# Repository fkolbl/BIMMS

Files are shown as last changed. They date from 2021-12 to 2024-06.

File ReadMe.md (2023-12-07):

# BIMMS
*Python library for controling [BIMMS](https://www.hardware-x.com/article/S2468-0672(22)00132-8/fulltext)*.

# Installation

use pip for installation : 
```
pip install bimms
```

# Requirements

Third party software (Waveform) has to be installed before BIMMS python API. 
BIMMS has been developped for python 3.
Required packages:
- numpy
- scipy
- matplotlib
- andi-py

for the third party softwares, please visit:
[Waveform](https://digilent.com/shop/software/digilent-waveforms/)

# TODO
    - Add selftests capabilities 
    - Add calibration routines --> skeleton OK 
    - Comments
    - add verbosity mode
    - do "standard configuration" 
    - add check_saturation 
    - add auto HIGH/LOW GAIN 
    - offset compensation in scope input

# HARDWARE TEST TODO:
    - Double check excitation/readout signaling 
    - test connect_TIA_to_CH2, disconnect_TIA_from_CH2, disable_current_source, enable_potentiostat
    - test dc feedback
    - Offset values are odds (measure seems ok tho)
    - Test Readout AC coupling (IA, TIA, etc) --> TIA AC COupling???

# Calibration todo
    - Offset calibration
    - DC calibration
    - OSL calibration

#TODO CONF AD2:
#SET in_channel_range_set --> 2.0,5.0 or 5.0 --> 2.0 by default; check if saturation?
#BS.ad2.in_average_filter_mode(-1)
#AD2 attenation = 1.0
#AD2 offsets = 0.0 
#Triggers --> AWG by default --> external TODO
#Conf modes (bode,)

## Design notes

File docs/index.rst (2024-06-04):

.. NeuRon Virtualizer (NRV) documentation master file, created by
   sphinx-quickstart on Sun Jul 23 14:36:32 2023.
   You can adapt this file completely to your liking, but it should at least
   contain the root `toctree` directive.

Welcome to BIMMS controling library's documentation!
====================================================

NRV (or NeuRon Virtualizer) is a pythonic framework to enable fast and user-friendly simulations of the Peripheral Nervous System. Axons models are simulated with the NEURON software, and extracellular fields are computed either from analytic equations such as point source approximation or with a more detailed description of the nerve and electrode geometry and Finite Elements Method, either using COMSOL (additional commercial license required) or the FENICS project. All computations are performed with the quasi-static approximation of the Maxwell equations, no ephaptic coupling. Stimulation waveform can be of random shapes, and any kinds of electrode can be combined to model complex stimulation strategies.

NRV is optimized for large population of axons, from generating correct population following a specific diameter distribution, through automatic placement to computation and post-processing of the axons' activity when a stimulus is applied. Parallel computation, interface with NEURON and COMSOL and FENICS is automatically handled by NRV.

NRV was developed by contributors from the CELL research group at the Laboratory ETIS (UMR CNRS 8051), ENSEA - CY Cergy Paris University, until june 2023 and is now developed and maintained by the Bioelectronics group of laboratory IMS (UMR CNRS 5218), INP Bordeaux, U. Bordeaux.

.. toctree::
   :maxdepth: 2
   :caption: Contents:

   introduction
..    installation
..    modules
..    changelog
..    devcorner

Indices and tables
==================

* :ref:`genindex`
* :ref:`modindex`
* :ref:`search`

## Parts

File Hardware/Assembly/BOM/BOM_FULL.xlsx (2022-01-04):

Designator | Qty | Manufacturer | Mfg Part | Description / Value | Package/Footprint
Q27,Q26 | 2 | Nexperia | PMT200EPEX | MOSFET 70V N- CHANNEL | SOT-223-3
Y1 | 1 | ABRACON | ABM8W-16.0000MHZ-7-D1X-T3 | Quartz CRYSTAL 16.0000MHZ 7PF SMD | 3.2x2.5mm
RV2 | 1 | Bourns | 3214W-1-503E | Trimmer Resistors SMD 4mm SQ 50K OHM | 3214J
RV1 | 1 | Bourns | 3214W-1-103E | Trimmer Resistors SMD 4mm SQ 10K OHM | 3214J
U8,U11,U12,U9 | 4 | Analog Devices | AD8250ARMZ | Amplificateurs d’instrumentation Hi Speed Programmable Gain In-Amp | MSOP-10
Q2,Q5,Q25,Q24,Q23,Q22,Q21,Q20,Q19,Q18,Q15,Q14,Q13,Q12,Q11,Q10,Q9,Q8,Q7,Q6,Q4,Q3,Q1 | 23 | Nexperia | NXV55UNR | MOSFET NCH 1A 100V 500MOHMS CPH3 | SOT-23-3
R38,R39,R75,R58,R12 | 5 | any/open | any/open | RES 1K OHM 1/8W 1% 0603 SMD | R_0603
R28,R27,R32,R31,R61,R60 | 6 | any/open | any/open | RES 39K OHM 1/8W 1% 0603 SMD | R_0603
K2,K5,K3,K23,K22,K21,K20,K19,K18,K17,K16,K15,K14,K13,K12,K11,K10,K9,K8,K7,K6,K4,K1 | 24 | KEMET | EE2-5NUH-L | Low Signal Relays - PCB 5V 10uA Relay Signal 2formC | EE2
R22,R50,R51,R23,R79,R106,R104,R102,R99,R98,R95,R92,R90,R88,R83,R78,R77,R73,R72,R71,R66,R64,R37,R10 | 23 | any/open | any/open | RES 100 OHM 1/8W 1% 0603 SMD | R_0603
R13,R15,R17,R14 | 4 | any/open | any/open | RES 10M OHM 1/8W 1% 0603 SMD | R_0603
R16,R20,R52,R48,R24,R44,R53,R49,R45,R25,R21,R18,R84,R105,R103,R101,R100,R97,R96,R94,R91,R89,R87,R82,R80,R76,R74,R70,R69,R65,R63,R35,R9,R5,R4,R1 | 36 | any/open | any/open | RES 10K OHM 1/8W 1% 0603 SMD | R_0603
R26,R29,R40,R46,R47,R41,R33,R30,R62,R59,R7,R6 | 12 | any/open | any/open | RES 4.7K OHM 1/8W 1% 0603 SMD | R_0603
D7,D14,D15,D8,D35,D34,D33,D32,D31,D30,D29,D27,D26,D25,D24,D23,D22,D21,D20,D17,D16,D11,D6 | 23 | ON Semiconductor | MBR0530T1G | Schottky Diodes & Rectifiers 0.5A 30V | SOD-123-2
D12,D9,D13,D10,D5,D4,D3,D1,D36,D28,D19,D18 | 12 | Wurth Elektronik | 150060VS75000 | Standard LEDs - SMD WL-SMCW SMDMono TpVw Waterclr 0603 BrtGrn | LED_0603
C65,C63,C27,C23,C20,C18,C49,C47,C66,C64,C28,C25,C50,C48,C21,C19,C79,C101,C90,C85,C84,C75,C73,C72,C61,C51,C45,C39,C17,C9,C8,C7,C6 | 33 | AVX | TAJB106K020SNJ | Tantalum Capacitors - Solid SMD 20V 10uF 10% 1210 ESR = 2.1 Ohm | CP_1210
C26 | 1 | any/open | any/open | MLCC - SMD/SMT 50V 4.7pF C0G 0603 | C_0603
C68,C67,C33,C31,C42,C41,C29,C22,C54,C52,C70,C69,C34,C32,C55,C53,C44,C43,C30,C24,C102,C100,C98,C97,C95,C94,C93,C92,C91,C89,C87,C86,C83,C82,C81,C78,C77,C76,C62,C56,C46,C40,C16,C15,C14,C13,C12,C11,C10,C4,C1 | 51 | any/open | any/open | CAP CER 100 nF 25V X7R 0603 | C_0603_1608Metric
C36,C35,C38,C37,C99,C96,C74,C71 | 8 | any/open | any/open | CAP CER 1 uF 25V X7R 0603 | C_0603_1608Metric
U5,U14,U6 | 3 | Analog Devices | LT1964ES5-BYP#TRPBF | LDO Voltage Regulators 200mA L/N Negative LDO in Thin SOT | TSOT-23-5
U3,U13,U4 | 3 | Analog Devices | LT1962EMS8#TRPBF | LDO Voltage Regulators 300mA Low Noise LDO | MSOP-8
U21 | 1 | Texas Instruments | TLV70233PDBVR | LDO Voltage Regulators 300mA Low-IQ LDO Reg | SOT-23-5
U20 | 1 | STMicroelectronics | STM32F103C6T6A | ARM Microcontrollers - MCU 32BIT Cortex M3 M/D 32 to 128 USB/CAN | LQFP-64
U16 | 1 | Analog Devices | LTC4416EMS#PBF | Power Management Specialised PMIC Dual PowerPath Controller | MSOP-10
U2 | 1 | Texas Instruments | OPA192IDR | Precision Amplifiers High VTG RRIO Prec Op Amps E-Trim | SOIC-8
SW3,SW2,SW1 | 3 | E-Switch | TL3305AF160QG | Tactile Switches 50mA 12VDC SPST, NO 3.8mm Act 160gf | 4.5x4.5 mm
R108,R107,R8,R3,R2 | 5 | any/open | any/open | RES 2K OHM 1/8W 1% 0603 SMD | R_0603_1608Metric
R93 | 1 | any/open | any/open | RES 3K3 OHM 1/8W 1% 0603 SMD | R_0603_1608Metric
R81 | 1 | any/open | any/open | RES 27 OHM 1/8W 1% 0603 SMD | R_0603_1608Metric
R56 | 1 | any/open | any/open | RES 1K OHM 1/8W 1% 0603 SMD | R_0603_1608Metric
R43,R42,R36,R34 | 4 | any/open | any/open | RES 390 OHM 1/8W 1% 0603 SMD | R_0603_1608Metric
R19 | 1 | any/open | any/open | RES 1K2 OHM 1/8W 1% 0603 SMD | R_0603_1608Metric
R11 | 1 | any/open | any/open | RES 1K8 OHM 1/8W 1% 0603 SMD | R_0603_1608Metric
L1,L3,L2 | 3 | Taiyo Yuden | CBC3225T100KR | Fixed Inductors 1210 10uH 172.9mOhms +/-10% 900mA HiCur | L_1210
C88 | 1 | any/open | any/open | CAP CER 4.7 nF 25V X7R 0603 | C_0603_1608Metric
C60,C59 | 2 | any/open | any/open | MLCC - SMD/SMT 50V 1pF C0G 0603 | C_0603_1608Metric
C5,C3 | 2 | any/open | any/open | MLCC - SMD/SMT 50V 30pF C0G 0603 | C_0603_1608Metric
U18,U17 | 2 | Analog Devices | AD830ARZ | Differential Amplifiers SOIC HI SPD, VIDEO DIFF OP AMP | SOIC-8
U15,U7 | 2 | Texas Instruments | THS4631 | High Speed Operational Amplifiers High Speed FET-Input Op Amp | SOIC-8
U10 | 1 | Texas Instruments | THS4151IDGK | Differential Amplifiers Fully Differential I/O High Slew Rate | VSSOP-8
R55,R54 | 2 | any/open | any/open | RES 10R OHM 1/8W 1% 0603 SMD | R_0603_1608Metric
D2,D37 | 2 | Wurth Elektronik | 150060SS55040 | Standard LEDs - SMD WL-SMCD SMD MonoChip 0603 Super Red 645nm | LED_0603
C57,C58 | 2 | any/open | any/open | MLCC - SMD/SMT 50V 10pF C0G 0603 | C_0603_1608Metric
R109 | 1 | any/open | any/open | RES 47k OHM 1/8W 1% 0603 SMD | R_0603_1608Metric
R68,R67 | 2 | any/open | any/open | RES 5k1 OHM 1/8W 1% 0603 SMD | R_0603_1608Metric
R57 | 1 | any/open | any/open | RES 1M OHM 1/8W 1% 0603 SMD | R_0603_1608Metric
U1 | 1 | tracopower | TDN 5-0922WI | TDN 5-0922WI | TDN 5-0922WI
U19 | 1 | tracopower | TEC 3-0911 | TEC_3-0911 | TEC 3-0910
C2 | 1 | any/open | any/open | 220 uF 25V | CP_Radial_D8.0mm_P5.00mm
J19,J9,J30,J31,J26,J28,J25,J27,J22,J21,J20,J10,J8,J7,J6,J29 | 16 | any/open | any/open | PCB Vertical SMA | PCB Vertical SMA
J4,J15,J5 | 3 | any/open | any/open | PinHeader_2x02_P2.54mm_Vertical | PinHeader_2x02_P2.54mm_Vertical
J33 | 1 | any/open | any/open | PinHeader_1x06_P2.54mm_Horizontal | PinHeader_1x06_P2.54mm_Horizontal
J18 | 1 | any/open | any/open | PinHeader_2x07_P2.54mm_Horizontal | PinHeader_2x07_P2.54mm_Horizontal
J16,JP4,JP3 | 3 | any/open | any/open | PinHeader_1x02_P2.54mm_Vertical | PinHeader_1x02_P2.54mm_Vertical
J32 | 1 | any/open | any/open | PinSocket_2x15_P2.54mm_Horizontal | PinSocket_2x15_P2.54mm_Horizontal
J29 | 1 | any/open | any/open | PinHeader_2x15_P2.54mm_Vertical | PinHeader_2x15_P2.54mm_Vertical
J23 | 1 | any/open | any/open | TerminalScrew_1x04_P2.54mm_Vertical | TerminalScrew_1x04_P2.54mm_Vertical
J13,J14,J24 | 3 | any/open | any/open | PinSocket_1x04_P2.54mm_Horizontal | PinSocket_1x04_P2.54mm_Horizontal
J11,J12 | 2 | any/open | any/open | PinSocket_2x03_P2.54mm_Horizontal | PinSocket_2x03_P2.54mm_Horizontal
J3 | 1 | any/open | any/open | PinSocket_1x03_P2.54mm_Horizontal | PinSocket_1x03_P2.54mm_Horizontal
J2 | 1 | any/open | any/open | PinHeader_2x05_P1.27mm_Vertical_SMD | PinHeader_2x05_P1.27mm_Vertical_SMD
J1 | 1 | CUI Devices | PJ-063BH | BarrelJack_CUI_PJ-063AH_Horizontal | BarrelJack_CUI_PJ-063AH_Horizontal
J17 | 1 | XKB Connectivity | U262-161N-4BVC11 | USB_C_Receptacle_XKB_U262-16XN-4BVC11 | USB_C_Receptacle_XKB_U262-16XN-4BVC11
F1 | 1 | any/open | any/open | Fuse_1206_3216Metric_Pad1.42x1.75mm_HandSolder | Fuse_1206_3216Metric_Pad1.42x1.75mm_HandSolder
Spacers Analog Discovery 2 | 4 | any/open | any/open | M3 x 10mm Fem/Fem | M3 x 10mm Fem/Fem
Spacers Board | 6 | any/open | any/open | M3 x 20mm Fem/Fem | M3 x 20mm Fem/Fem
Con Analog Discovery 2 | 2 | any/open | any/open | Headers & Wire Housings .1CL IDC REC 2X15P MIL 30AU | Headers & Wire Housings .1CL IDC REC 2X15P MIL 30AU
PCB screws | 20 | any/open | any/open | M3 x 4mm | M3 x 4mm

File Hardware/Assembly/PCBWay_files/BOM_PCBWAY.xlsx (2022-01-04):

 |  |  | xxxx xxxx xxxxx xxPCS BOM (Sample Bill of Materials)
Item # | *Designator | *Qty | Manufacturer | *Mfg Part # | Description / Value | *Package/Footprint | Type | Your Instructions / Notes
1 | Q26,Q27 | 2 | Nexperia | PMT200EPEX | MOSFET 70V N- CHANNEL | SOT-223-3 | SMD
2 | Y1 | 1 | ABRACON | ABM8W-16.0000MHZ-7-D1X-T3 | Quartz CRYSTAL 16.0000MHZ 7PF SMD | 3.2x2.5mm | SMD
3 | RV2 | 1 | Bourns | 3214W-1-503E | Trimmer Resistors SMD 4mm SQ 50K OHM | 3214J | SMD
4 | RV1 | 1 | Bourns | 3214W-1-103E | Trimmer Resistors SMD 4mm SQ 10K OHM | 3214J | SMD
5 | U8,U11,U12,U9 | 4 | Analog Devices | AD8250ARMZ | Amplificateurs d’instrumentation Hi Speed Programmable Gain In-Amp | MSOP-10 | SMD
6 | Q2,Q5,Q25,Q24,Q23,Q22,Q21,Q20,Q19,Q18,Q15,Q14,Q13,Q12,Q11,Q10,Q9,Q8,Q7,Q6,Q4,Q3,Q1 | 23 | Nexperia | NXV55UNR | MOSFET NCH 1A 100V 500MOHMS CPH3 | SOT-23-3 | SMD
7 | R38,R39,R75,R58,R12 | 5 | any/open | any/open | RES 1K OHM 1/8W 1% 0603 SMD | R_0603 | SMD
8 | R28,R27,R32,R31,R61,R60 | 6 | any/open | any/open | RES 39K OHM 1/8W 1% 0603 SMD | R_0603 | SMD
9 | K2,K5,K3,K23,K22,K21,K20,K19,K18,K17,K16,K15,K14,K13,K12,K11,K10,K9,K8,K7,K6,K4,K1 | 23 | KEMET | EE2-5NUH-L | Low Signal Relays - PCB 5V 10uA Relay Signal 2formC | EE2 | SMD
10 | R22,R50,R51,R23,R79,R106,R104,R102,R99,R98,R95,R92,R90,R88,R83,R78,R77,R73,R72,R71,R66,R64,R37,R10 | 24 | any/open | any/open | RES 100 OHM 1/8W 1% 0603 SMD | R_0603 | SMD
11 | R13,R15,R17,R14 | 4 | any/open | any/open | RES 10M OHM 1/8W 1% 0603 SMD | R_0603 | SMD
12 | R16,R20,R52,R48,R24,R44,R53,R49,R45,R25,R21,R18,R84,R105,R103,R101,R100,R97,R96,R94,R91,R89,R87,R82,R80,R76,R74,R70,R69,R65,R63,R35,R9,R5,R4,R1 | 36 | any/open | any/open | RES 10K OHM 1/8W 1% 0603 SMD | R_0603 | SMD
13 | R26,R29,R40,R46,R47,R41,R33,R30,R62,R59,R7,R6 | 12 | any/open | any/open | RES 4.7K OHM 1/8W 1% 0603 SMD | R_0603 | SMD
14 | D7,D14,D15,D8,D35,D34,D33,D32,D31,D30,D29,D27,D26,D25,D24,D23,D22,D21,D20,D17,D16,D11,D6 | 23 | ON Semiconductor | MBR0530T1G | Schottky Diodes & Rectifiers 0.5A 30V | SOD-123-2 | SMD
15 | D12,D9,D13,D10,D5,D4,D3,D1,D36,D28,D19,D18 | 12 | Wurth Elektronik | 150060VS75000 | Standard LEDs - SMD WL-SMCW SMDMono TpVw Waterclr 0603 BrtGrn | LED_0603 | SMD
16 | C65,C63,C27,C23,C20,C18,C49,C47,C66,C64,C28,C25,C50,C48,C21,C19,C79,C101,C90,C85,C84,C75,C73,C72,C61,C51,C45,C39,C17,C9,C8,C7,C6 | 33 | AVX | TAJB106K020SNJ | Tantalum Capacitors - Solid SMD 20V 10uF 10% 1210 ESR = 2.1 Ohm | CP_1210 | SMD
17 | C26 | 1 | any/open | any/open | MLCC - SMD/SMT 50V 4.7pF C0G 0603 | C_0603 | SMD
18 | C68,C67,C33,C31,C42,C41,C29,C22,C54,C52,C70,C69,C34,C32,C55,C53,C44,C43,C30,C24,C102,C100,C98,C97,C95,C94,C93,C92,C91,C89,C87,C86,C83,C82,C81,C78,C77,C76,C62,C56,C46,C40,C16,C15,C14,C13,C12,C11,C10,C4,C1 | 51 | any/open | any/open | CAP CER 100 nF 25V X7R 0603 | C_0603_1608Metric | SMD
19 | C36,C35,C38,C37,C99,C96,C74,C71 | 8 | any/open | any/open | CAP CER 1 uF 25V X7R 0603 | C_0603_1608Metric | SMD
20 | U5,U14,U6 | 3 | Analog Devices | LT1964ES5-BYP#TRPBF | LDO Voltage Regulators 200mA L/N Negative LDO in Thin SOT | TSOT-23-5 | SMD
21 | U3,U13,U4 | 3 | Analog Devices | LT1962EMS8#TRPBF | LDO Voltage Regulators 300mA Low Noise LDO | MSOP-8 | SMD
22 | U21 | 1 | Texas Instruments | TLV70233PDBVR | LDO Voltage Regulators 300mA Low-IQ LDO Reg | SOT-23-5 | SMD
23 | U20 | 1 | STMicroelectronics | STM32F103R6T6A | ARM Microcontrollers - MCU 32BIT Cortex M3 M/D 32 to 128 USB/CAN | LQFP-64 | SMD
24 | U16 | 1 | Analog Devices | LTC4416EMS#PBF | Power Management Specialised PMIC Dual PowerPath Controller | MSOP-10 | SMD
25 | U2 | 1 | Texas Instruments | OPA192IDR | Precision Amplifiers High VTG RRIO Prec Op Amps E-Trim | SOIC-8 | SMD
26 | SW3,SW2,SW1 | 3 | E-Switch | TL3305AF160QG | Tactile Switches 50mA 12VDC SPST, NO 3.8mm Act 160gf | 4.5x4.5 mm | SMD
27 | R108,R107,R8,R3,R2 | 5 | any/open | any/open | RES 2K OHM 1/8W 1% 0603 SMD | R_0603_1608Metric | SMD
28 | R93 | 1 | any/open | any/open | RES 3K3 OHM 1/8W 1% 0603 SMD | R_0603_1608Metric | SMD
29 | R81 | 1 | any/open | any/open | RES 27 OHM 1/8W 1% 0603 SMD | R_0603_1608Metric | SMD
30 | R56 | 1 | any/open | any/open | RES 1K OHM 1/8W 1% 0603 SMD | R_0603_1608Metric | SMD
31 | R43,R42,R36,R34 | 4 | any/open | any/open | RES 390 OHM 1/8W 1% 0603 SMD | R_0603_1608Metric | SMD
32 | R19 | 1 | any/open | any/open | RES 1K2 OHM 1/8W 1% 0603 SMD | R_0603_1608Metric | SMD
33 | R11 | 1 | any/open | any/open | RES 1K8 OHM 1/8W 1% 0603 SMD | R_0603_1608Metric | SMD
34 | L1,L3,L2 | 3 | Taiyo Yuden | CBC3225T100KR | Fixed Inductors 1210 10uH 172.9mOhms +/-10% 900mA HiCur | L_1210 | SMD
35 | C88 | 1 | any/open | any/open | CAP CER 4.7 nF 25V X7R 0603 | C_0603_1608Metric | SMD
36 | C60,C59 | 2 | any/open | any/open | MLCC - SMD/SMT 50V 1pF C0G 0603 | C_0603_1608Metric | SMD
37 | C5,C3 | 2 | any/open | any/open | MLCC - SMD/SMT 50V 30pF C0G 0603 | C_0603_1608Metric | SMD
38 | U18,U17 | 2 | Analog Devices | AD830ARZ | Differential Amplifiers SOIC HI SPD, VIDEO DIFF OP AMP | SOIC-8 | SMD
39 | U15,U7 | 2 | Texas Instruments | THS4631D | High Speed Operational Amplifiers High Speed FET-Input Op Amp | SOIC-8 | SMD
40 | U10 | 1 | Texas Instruments | THS4151IDGNR | Differential Amplifiers Fully Differential I/O High Slew Rate | VSSOP-8 | SMD
41 | R55,R54 | 2 | any/open | any/open | RES 10R OHM 1/8W 1% 0603 SMD | R_0603_1608Metric | SMD
42 | D2,D37 | 2 | Wurth Elektronik | 150060SS55040 | Standard LEDs - SMD WL-SMCD SMD MonoChip 0603 Super Red 645nm | LED_0603 | SMD
43 | C57,C58 | 2 | any/open | any/open | MLCC - SMD/SMT 50V 10pF C0G 0603 | C_0603_1608Metric | SMD
44 | R109 | 1 | any/open | any/open | RES 47k OHM 1/8W 1% 0603 SMD | R_0603_1608Metric | SMD
45 | R68,R67 | 2 | any/open | any/open | RES 5k1 OHM 1/8W 1% 0603 SMD | R_0603_1608Metric | SMD
46 | R57 | 1 | any/open | any/open | RES 1M OHM 1/8W 1% 0603 SMD | R_0603_1608Metric | SMD

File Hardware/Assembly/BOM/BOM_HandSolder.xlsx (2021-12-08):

Designator | Package | Quantity | Designation | Supplier | Ref | unit Price | Price
U1 | TDN 5-0922WI | 1 | TDN 5-0922WI | Mouser | 495-TDN5-0922WI | 22.02 | 22.02
U19 | TEC 3-0910 | 1 | TEC_3-0911 | Mouser | 495-TEC3-0911 | 10.27 | 10.27
C2 | CP_Radial_D8.0mm_P5.00mm | 1 | 220 uF 25V | Mouser | 661-ELXZ250ETC221MH1 | 0.508 | 0.508
J19,J9,J30,J31,J26,J28,J25,J27,J22,J21,J20,J10,J8,J7,J6,J29 | PCB Vertical SMA | 16 | PCB Vertical SMA | Mouser | 471-SMACONNECTOR | 1.33 | 21.28
J4,J15,J5 | PinHeader_2x02_P2.54mm_Vertical | 3 | PinHeader_2x02_P2.54mm_Vertical | Mouser | 571-5-146250-2 | 0.306 | 0.918
J33 | PinHeader_1x06_P2.54mm_Horizontal | 1 | PinHeader_1x06_P2.54mm_Horizontal | Mouser | 571-826947-6 | 0.5 | 0.5
J18 | PinHeader_2x07_P2.54mm_Horizontal | 1 | PinHeader_2x07_P2.54mm_Horizontal | Mouser | 200-SSQ10702GDRA | 2.24 | 2.24
J16,JP4,JP3 | PinHeader_1x02_P2.54mm_Vertical | 3 | PinHeader_1x02_P2.54mm_Vertical | Mouser | 571-826936-2 | 0.207 | 0.621
J32 | PinSocket_2x15_P2.54mm_Horizontal | 1 | PinSocket_2x15_P2.54mm_Horizontal | Mouser | 200-SSQ11502TDRA | 2.57 | 2.57
J29 | PinHeader_2x15_P2.54mm_Vertical | 1 | PinHeader_2x15_P2.54mm_Vertical | Mouser | 649-77313-801-30LF | 0.99 | 0.99
J23 | Molex_KK-254_AE-6410-04A_1x04_P2.54mm_Vertical | 1 | Molex_KK-254_AE-6410-04A_1x04_P2.54mm_Vertical | Mouser | 571-282834-4 | 2.4 | 2.4
J13,J14,J24 | PinSocket_1x04_P2.54mm_Horizontal | 3 | PinSocket_1x04_P2.54mm_Horizontal | Mouser | 200-SSQ10404SSRA | 1.37 | 4.11
J11,J12 | PinSocket_2x03_P2.54mm_Horizontal | 2 | PinSocket_2x03_P2.54mm_Horizontal | Mouser | 200-SSQ10302GDRA | 1.53 | 3.06
J3 | PinSocket_1x03_P2.54mm_Horizontal | 1 | PinSocket_1x03_P2.54mm_Horizontal | Mouser | 200-SSQ10302SSRA | 0.999 | 0.999
J2 | PinHeader_2x05_P1.27mm_Vertical_SMD | 1 | PinHeader_2x05_P1.27mm_Vertical_SMD | Mouser | 485-752 | 1.27 | 1.27
J1 | BarrelJack_CUI_PJ-063AH_Horizontal | 1 | BarrelJack_CUI_PJ-063AH_Horizontal | Mouser | 490-PJ-063BH | 1.22 | 1.22
J17 | USB_C_Receptacle_XKB_U262-16XN-4BVC11 | 1 | USB_C_Receptacle_XKB_U262-16XN-4BVC11 | LCSC | C319148 | 0.37 | 0.37
F1 | Fuse_1206_3216Metric_Pad1.42x1.75mm_HandSolder | 1 | Fuse_1206_3216Metric_Pad1.42x1.75mm_HandSolder | Mouser | 576-0466.500NR | 0.65 | 0.65
Spacers Analog Discovery 2 | M3 x 10mm Fem/Fem | 4 | M3 x 10mm Fem/Fem | Mouser | 710-970100321 | 0.36 | 1.44
Spacers Board | M3 x 20mm Fem/Fem | 6 | M3 x 20mm Fem/Fem | Mouser | 710-970200354 | 0.567 | 3.402
Con Analog Discovery 2 | Headers & Wire Housings .1CL IDC REC 2X15P MIL 30AU | 2 | Headers & Wire Housings .1CL IDC REC 2X15P MIL 30AU | Mouser | 571-1658623-7 | 2.41 | 4.82
PCB screws | M3 x 4mm | 20 | M3 x 4mm | Mouser | 481-0263 | 0.16 | 3.2

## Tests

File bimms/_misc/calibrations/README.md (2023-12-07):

Here will be store the calibration data in json files

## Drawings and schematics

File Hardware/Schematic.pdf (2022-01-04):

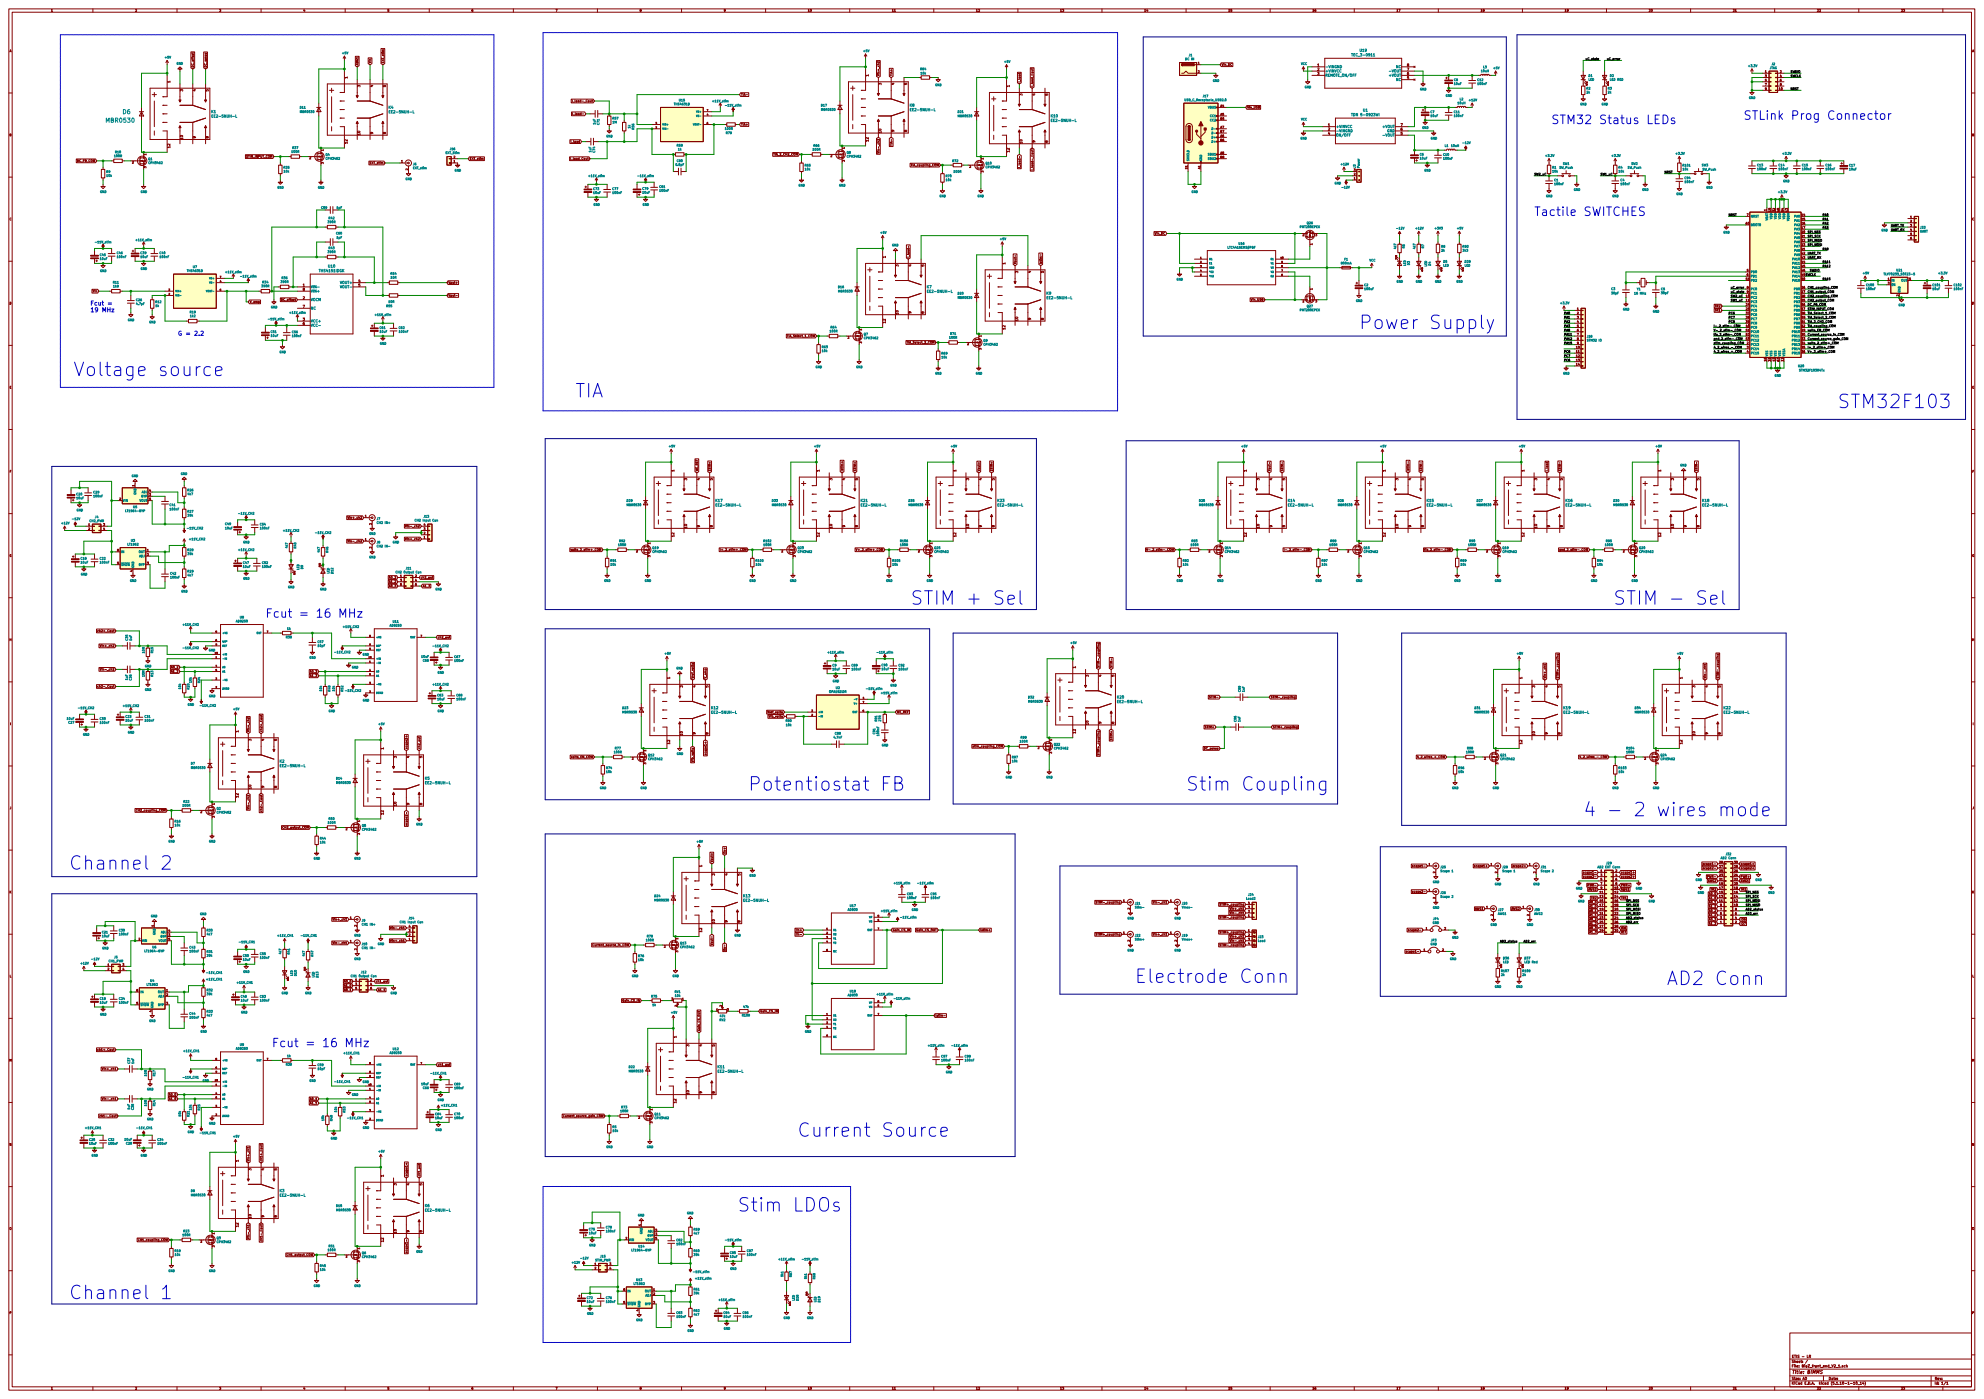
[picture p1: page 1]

STLink Prog Connector STM32 Status LEDs

1 VIN 2 BYP 3 ADJ 4 VOUT 5 U5

scope2- Vin+_ch1 Vin+_ch1 Vin+_ch1 Vin-_ch1

1 VIN 2 BYP 3 ADJ 4 VOUT 5 U6

File: BioZ_front_end_V2_1.sch Sheet: / ETIS - LR

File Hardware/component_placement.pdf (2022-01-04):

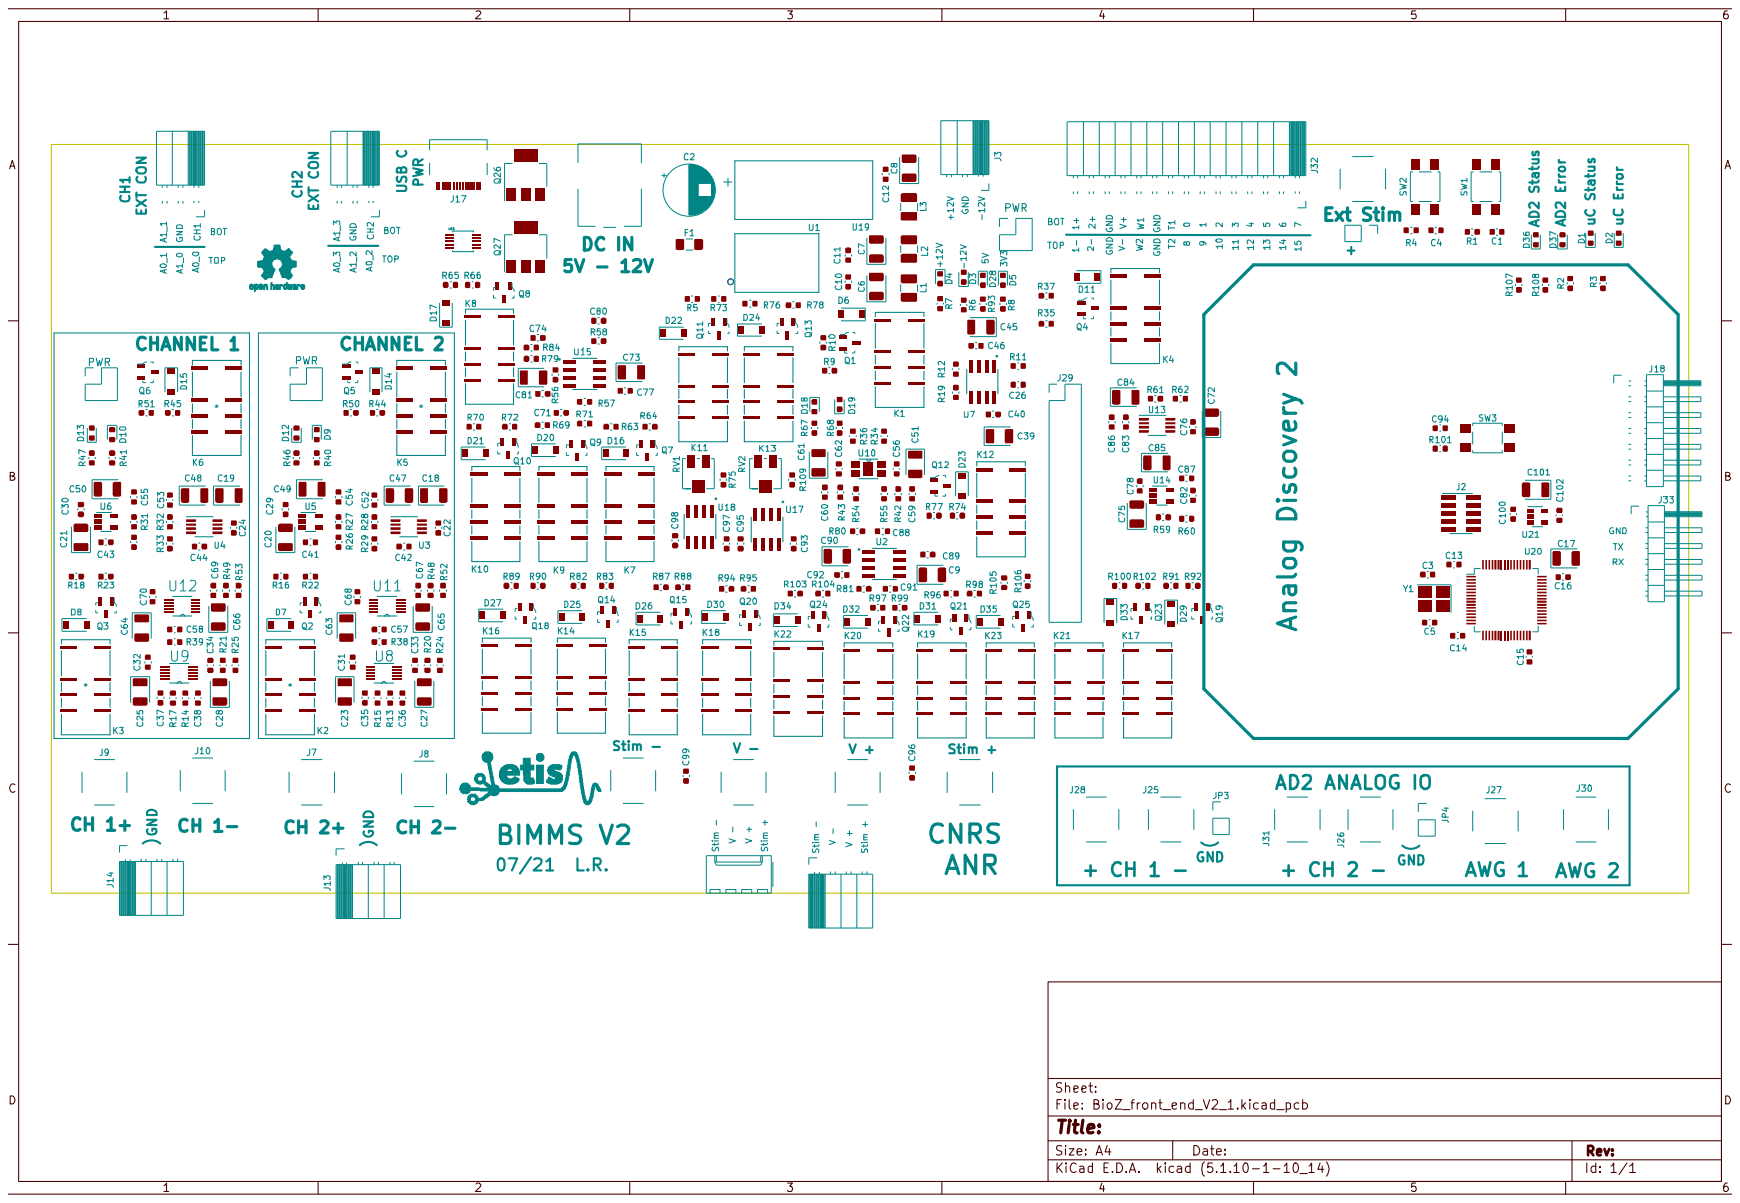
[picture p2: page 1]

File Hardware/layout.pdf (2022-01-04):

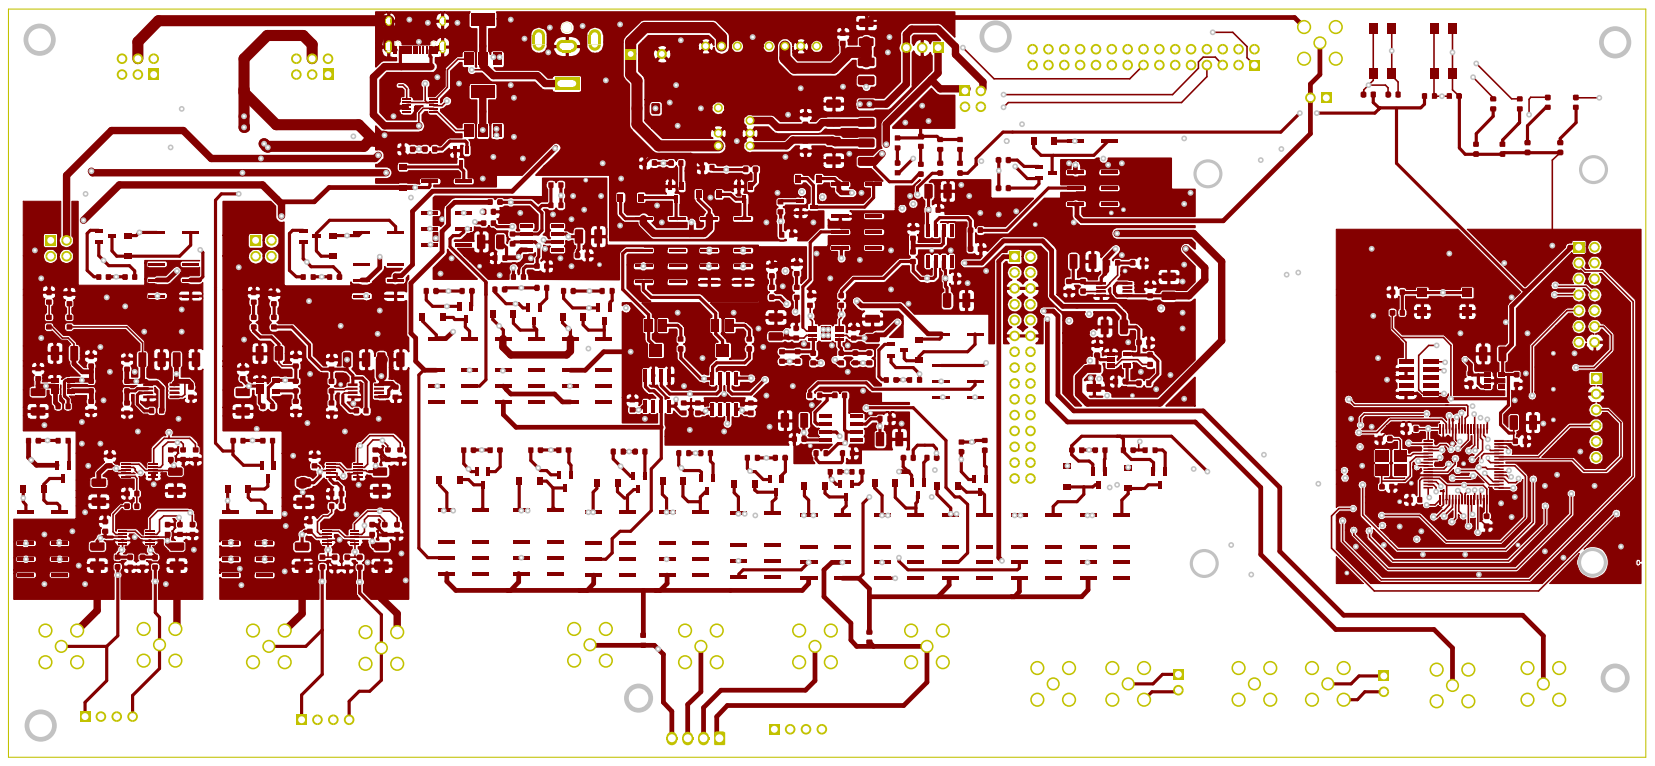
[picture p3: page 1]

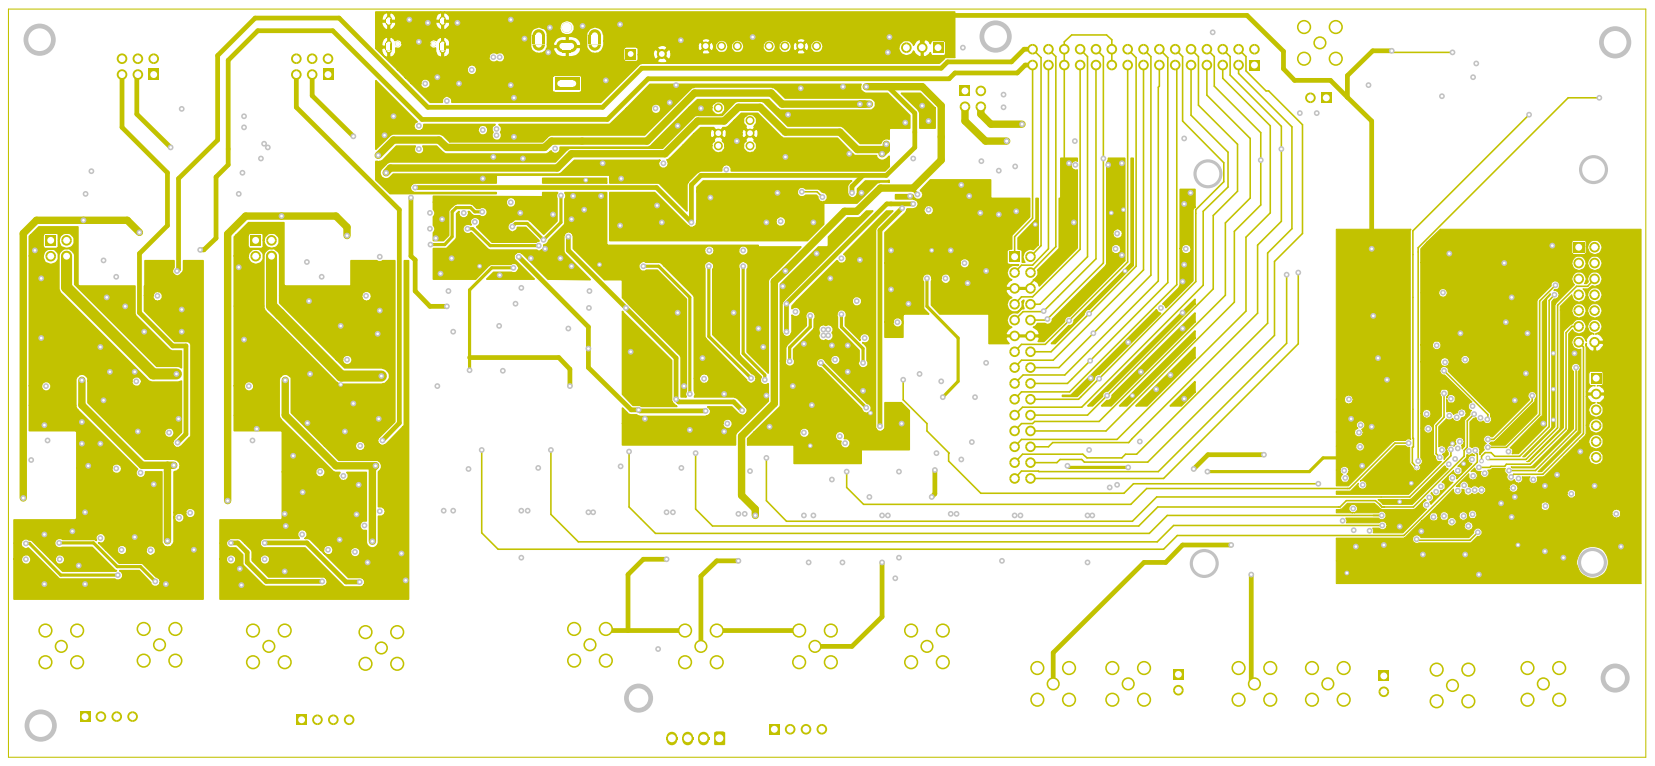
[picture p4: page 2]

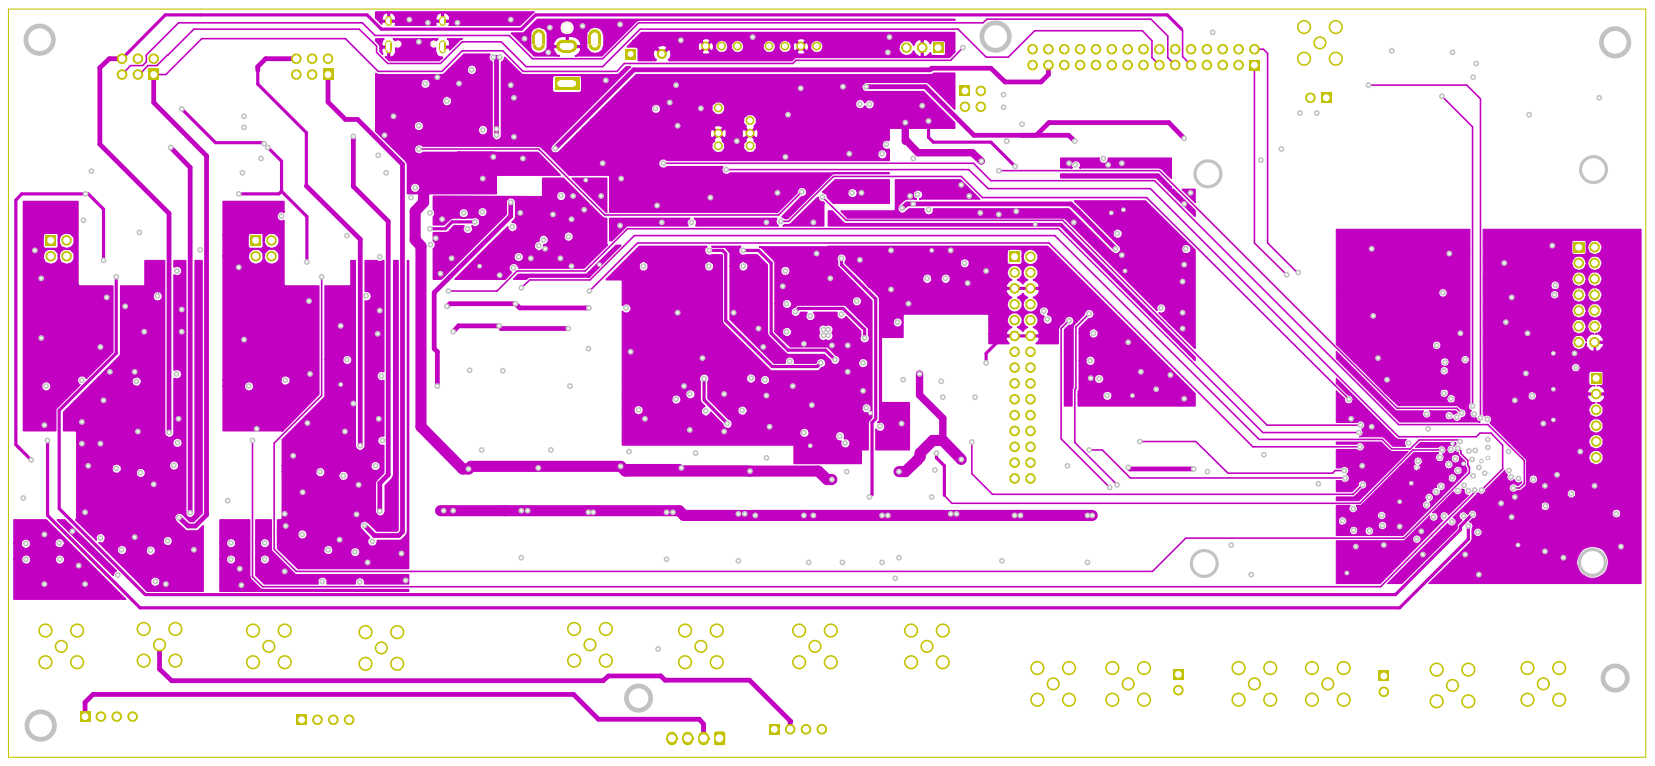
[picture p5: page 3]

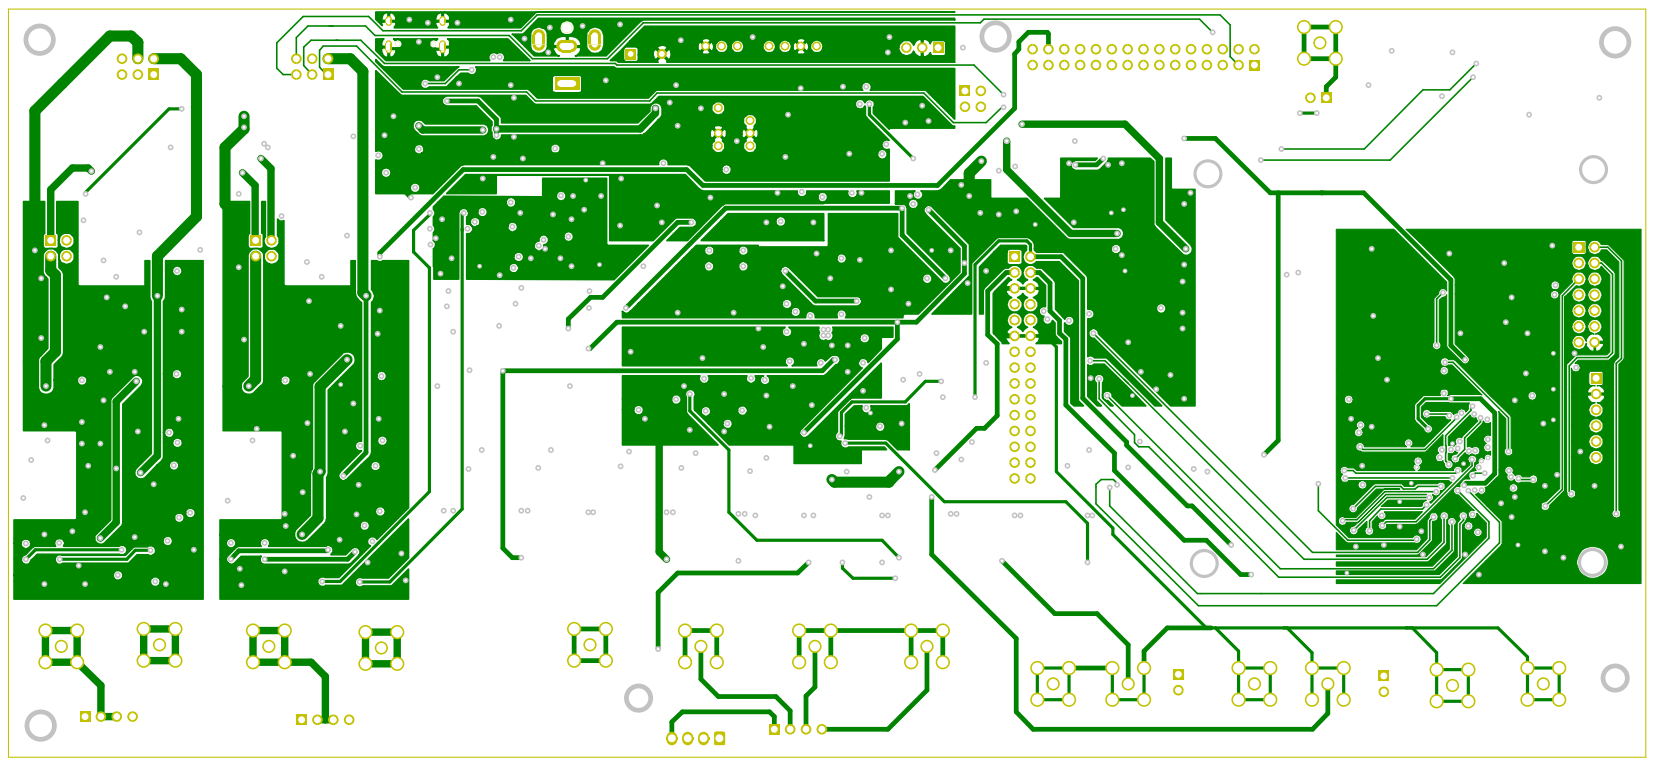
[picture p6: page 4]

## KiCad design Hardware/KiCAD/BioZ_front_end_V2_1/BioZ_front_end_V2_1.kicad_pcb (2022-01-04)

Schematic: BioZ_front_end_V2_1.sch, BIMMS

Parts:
C1, C4, C10, C11, C12, C13, C14, C15, C16, C22, C24, C29, C30, C31, C32, C33, C34, C40, C41, C42, C43, C44, C46, C52, C53, C54, C55, C56, C62, C67, C68, C69, C70, C76, C77, C78, C81, C82, C83, C86, C87, C89, C91, C92, C93, C94, C95, C97, C98, C100, C102: 100nF; C_0603_1608Metric
C2: 100uF; CP_Radial_D8.0mm_P5.00mm
C3, C5: 30pF; C_0603_1608Metric
C6, C7, C8, C9, C17, C18, C19, C20, C21, C23, C25, C27, C28, C39, C45, C47, C48, C49, C50, C51, C61, C63, C64, C65, C66, C72, C73, C75, C79, C84, C85, C90, C101: 10uF; CP_EIA-3528-21_Kemet-B
C26: 4.7pF; C_0603_1608Metric
C35, C36, C37, C38, C71, C74, C96, C99: 1uF; C_0603_1608Metric
C57, C58: 10pF; C_0603_1608Metric
C59, C60: 1pF; C_0603_1608Metric
C80: 0.5pF; C_0603_1608Metric
C88: 4.7nF; C_0603_1608Metric
D1, D3, D4, D5, D9, D10, D12, D13, D18, D19, D28, D36: LED; LED_0603_1608Metric
D2: LED RED; LED_0603_1608Metric
D6, D7, D8, D11, D14, D15, D16, D17, D20, D21, D22, D23, D24, D25, D26, D27, D29, D30, D31, D32, D33, D34, D35: MBR0530; D_SOD-123
D37: LED Red; LED_0603_1608Metric
F1: 800mA; Fuse_1206_3216Metric_Pad1.42x1.75mm_HandSolder
J1: DC IN; BarrelJack_CUI_PJ-063AH_Horizontal
J2: JTAG; PinHeader_2x05_P1.27mm_Vertical_SMD
J3: Power; PinSocket_1x03_P2.54mm_Horizontal; MPN 640456-3; Digi-Key_PN A19470-ND
J4: CH2_PWR; PinHeader_2x02_P2.54mm_Vertical
J5: CH1_PWR; PinHeader_2x02_P2.54mm_Vertical
J6: EXT_stim; SMA_Amphenol_132291_Vertical
J7: CH2 IN+; SMA_Amphenol_132291_Vertical
J8: CH2 IN-; SMA_Amphenol_132291_Vertical
J9: CH1 IN+; SMA_Amphenol_132291_Vertical
J10: CH1 IN-; SMA_Amphenol_132291_Vertical
J11: CH2 Output Con; PinSocket_2x03_P2.54mm_Horizontal
J12: CH1 Output Con; PinSocket_2x03_P2.54mm_Horizontal
J13: CH2 Input Con; PinSocket_1x04_P2.54mm_Horizontal
J14: CH1 Input Con; PinSocket_1x04_P2.54mm_Horizontal
J15: STIM_PWR; PinHeader_2x02_P2.54mm_Vertical
J16: EXT_Stim; PinHeader_1x02_P2.54mm_Vertical
J17: USB_C_Receptacle_USB2.0; USB_C_Receptacle_XKB_U262-16XN-4BVC11
J18: STM32 IO; PinHeader_2x07_P2.54mm_Horizontal
J19: Vmes+; SMA_Amphenol_132291_Vertical
J20: Vmes-; SMA_Amphenol_132291_Vertical
J21: Stim-; SMA_Amphenol_132291_Vertical
J22: Stim+; SMA_Amphenol_132291_Vertical
J23: Load; Molex_KK-254_AE-6410-04A_1x04_P2.54mm_Vertical
J24: Load2; PinSocket_1x04_P2.54mm_Horizontal
J25, J28: Scope 1; SMA_Amphenol_132291_Vertical
J26, J31: Scope 2; SMA_Amphenol_132291_Vertical
J27: AWG1; SMA_Amphenol_132291_Vertical
J29: AD2 EXT Conn; PinHeader_2x15_P2.54mm_Vertical
J30: AWG2; SMA_Amphenol_132291_Vertical
J32: AD2 Conn; PinSocket_2x15_P2.54mm_Horizontal
J33: UART; PinHeader_1x06_P2.54mm_Horizontal
JP3, JP4: GND; PinHeader_1x02_P2.54mm_Vertical
K1, K2, K3, K4, K5, K6, K7, K8, K9, K10, K11, K12, K13, K14, K15, K16, K17, K18, K19, K20, K21, K22, K23: EE2-5NUH-L
L1, L2, L3: 10uH; L_1210_3225Metric_Pad1.42x2.65mm_HandSolder
Q1, Q2, Q3, Q4, Q5, Q6, Q7, Q8, Q9, Q10, Q11, Q12, Q13, Q14, Q15, Q18, Q19, Q20, Q21, Q22, Q23, Q24, Q25: CPH3462
Q26, Q27: PMT200EPEX; SOT-223-3_TabPin2
R1, R4, R5, R9, R16, R18, R20, R21, R24, R25, R35, R44, R45, R48, R49, R52, R53, R63, R65, R69, R70, R74, R76, R80, R82, R84, R87, R89, R91, R94, R96, R97, R100, R101, R103, R105: 10k; R_0603_1608Metric
R2, R3, R8, R107, R108: 2k; R_0603_1608Metric
R6, R7, R26, R29, R30, R33, R40, R41, R46, R47, R59, R62: 4k7; R_0603_1608Metric
R10, R22, R23, R37, R50, R51, R64, R66, R71, R72, R73, R77, R78, R79, R83, R88, R90, R92, R95, R98, R99, R102, R104, R106: 100R; R_0603_1608Metric
R11: 1k8; R_0603_1608Metric
R12, R38, R39, R56, R58, R75: 1k; R_0603_1608Metric
R13, R14, R15, R17: 10M; R_0603_1608Metric
R19: 1k2; R_0603_1608Metric
R27, R28, R31, R32, R60, R61: 39k; R_0603_1608Metric
R34, R36, R42, R43: 390R; R_0603_1608Metric
R54, R55: 10R; R_0603_1608Metric
R57: 1M; R_0603_1608Metric
R67, R68: 5k1; R_0603_1608Metric
R81: 27R; R_0603_1608Metric
R93: 3k3; R_0603_1608Metric
R109: 47k; R_0603_1608Metric
RV1: 10k; Potentiometer_Bourns_3214J_Horizontal
RV2: 47k; Potentiometer_Bourns_3214J_Horizontal
SW1, SW2, SW3: SW_Push; SW_SPST_TL3305A
U1: TDN 5-0923WI; TDN 5-0910WI
U2: OPA192IDR; SOIC127P599X175-8N
U3, U4, U13: LT1962; MSOP-8_3x3mm_P0.65mm
U5, U6, U14: LT1964-BYP; TSOT-23-5
U7, U15: THS4631D; SOIC127P599X175-8N
U8, U9, U11, U12: AD8250; SOP50P490X110-10N
U10: THS4151IDGK
U16: LTC4416EMS#PBF; MSOP-10_MS; MANUFACTURER_PART_NUMBER ltc4416ims1
U17, U18: AD830; SOIC127P600X175-8N
U19: TEC_3-0911; TEC 3-0910
U20: STM32F103R4Tx; LQFP-64_10x10mm_P0.5mm
U21: TLV70233_SOT23-5; SOT-23-5
Y1: 16 MHz; Crystal_SMD_3225-4Pin_3.2x2.5mm_HandSoldering

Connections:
4_2_wires_+_COM: R96.1, R98.2, U20.4 (PC15)
4_2_wires_-_COM: R103.1, R104.2, U20.3 (PC14)
+5VA: C100.1, D6.1 (K), D7.1 (K), D8.1 (K), D11.1 (K), D14.1 (K), D15.1 (K), D16.1 (K), D17.1 (K), D20.1 (K), D21.1 (K), D22.1 (K), D23.1 (K), D24.1 (K), D25.1 (K), D26.1 (K), D27.1 (K), D29.1 (K), D30.1 (K), D31.1 (K), D32.1 (K), D33.1 (K), D34.1 (K), D35.1 (K), K1.1, K2.1, K3.1, K4.1, K5.1, K6.1, K7.1, K8.1, K9.1, K10.1, K11.1, K12.1, K13.1, K14.1, K15.1, K16.1, K17.1, K18.1, K19.1, K20.1, K21.1, K22.1, K23.1, L3.2, R93.1, U21.1 (IN), U21.3 (EN)
+12V: J3.3, J4.2, J5.2, J15.2, L2.2, R7.2
+14V5_CH1: C25.1, C32.1, C44.1, C48.1, C53.1, C64.1, C70.1, R32.1, R41.2, U4.1 (OUT), U9.8 (+VS), U12.8 (+VS)
+14V5_CH2: C23.1, C31.1, C42.1, C47.1, C52.1, C63.1, C68.1, R28.1, R40.2, U3.1 (OUT), U8.8 (+VS), U11.8 (+VS)
+14V5_stim: C9.1, C39.1, C40.1, C61.1, C62.1, C73.1, C77.1, C83.1, C84.1, C86.1, C89.1, C93.1, C97.1, R61.1, R67.2, U2.7 (V+), U7.7 (VS+), U10.3 (VCC+), U13.1 (OUT), U15.7 (VS+), U17.8 (VP), U18.8 (VP)
-12V: J3.1, J4.1, J5.1, J15.1, L1.2, R6.2
-14V5_stim: C45.2, C46.1, C51.2, C56.1, C79.2, C81.1, C82.2, C85.2, C87.1, C90.2, C92.1, C95.1, C98.1, R60.2, R68.2, U2.4 (-V), U7.4 (VS-), U10.6 (VCC-), U14.5 (VOUT), U15.4 (VS-), U17.5 (VN), U18.5 (VN)
/AD2_err: D37.2 (A), J29.26, J32.6
/AD2_status: D36.2 (A), J29.24, J32.8
/NRST: C94.2, J2.10, R101.2, SW3.1, U20.7 (NRST)
/PA0: J18.2, U20.14 (PA0)
/PA1: J18.3, U20.15 (PA1)
/PA2: J18.4, U20.16 (PA2)
/PA3: J18.5, U20.17 (PA3)
/PA8: J18.6, U20.41 (PA8)
/PA11: J18.7, U20.44 (PA11)
/PA12: J18.8, U20.45 (PA12)
/PA15: J18.9, U20.50 (PA15)
/PC6: J18.13, U20.37 (PC6)
/PC7: J18.12, U20.38 (PC7)
/PC8: J18.11, U20.39 (PC8)
/SPI_MISO: J29.22, J32.10, U20.22 (PA6)
/SPI_MOSI: J29.20, J32.12, U20.23 (PA7)
/SPI_NSS: J29.16, J32.16, U20.20 (PA4)
/SPI_SCK: J29.18, J32.14, U20.21 (PA5)
/SW1_uC: C4.2, R4.2, SW2.1, U20.11 (PC3)
/SW2_uC: C1.2, R1.2, SW1.1, U20.10 (PC2)
/SWCLK: J2.4, U20.49 (PA14)
/SWDIO: J2.2, U20.46 (PA13)
/UART_RX: J33.4, U20.43 (PA10)
/UART_TX: J33.3, U20.42 (PA9)
/uC_error: D2.2 (A), U20.8 (PC0)
/uC_state: D1.2 (A), U20.9 (PC1)
A0_0: J12.1, J29.15, J32.15, R21.2, U9.4 (A0)
A0_1: J12.5, J29.19, J32.11, R49.2, U12.4 (A0)
A0_2: J11.1, J29.23, J32.7, R20.2, U8.4 (A0)
A0_3: J11.5, J29.27, J32.3, R48.2, U11.4 (A0)
A1_0: J12.3, J29.17, J32.13, R25.2, U9.5 (A1)
A1_1: J12.6, J29.21, J32.9, R53.2, U12.5 (A1)
A1_2: J11.3, J29.25, J32.5, R24.2, U8.5 (A1)
A1_3: J11.6, J29.29, J32.1, R52.2, U11.5 (A1)
AWG1: J27.1 (In), J29.10, J32.22, K4.3 (2)
AWG2: J29.9, J30.1 (In), J32.21
CH1_coupling_COM: R18.1, R23.2, U20.26 (PB0)
CH1_output_COM: R45.1, R51.2, U20.27 (PB1)
CH2_coupling_COM: R16.1, R22.2, U20.28 (PB2)
CH2_output_COM: R44.1, R50.2, U20.55 (PB3)
Current_source_gain_COM: R5.1, R73.2, U20.33 (PB12)
Current_source_in_COM: R76.1, R78.2, U20.30 (PB11)
DC_FB_COM: R9.1, R10.2, U20.56 (PB4)
DC_offset: K1.4 (3), U10.2 (VOCM)
DC_sense: C96.1, K1.5 (4), K17.5 (4), K20.8 (5), K21.5 (4), K23.5 (4)
EXT_stim: J6.1 (In), J16.2, K4.5 (4)
GND: C1.1, C2.2, C3.1, C4.1, C5.1, C6.1, C7.2, C8.2, C9.2, C10.2, C11.2, C12.2, C13.1, C14.1, C15.1, C16.1, C17.2, C18.2, C19.2, C20.1, C21.1, C22.2, C23.2, C24.2, C25.2, C26.2, C27.1, C28.1, C29.2, C30.2, C31.2, C32.2, C33.2, C34.2, C39.2, C40.2, C45.1, C46.2, C47.2, C48.2, C49.1, C50.1, C51.1, C52.2, C53.2, C54.2, C55.2, C56.2, C57.2, C58.2, C61.2, C62.2, C63.2, C64.2, C65.1, C66.1, C67.2, C68.2, C69.2, C70.2, C72.2, C73.2, C75.1, C76.2, C77.2, C78.2, C79.1, C81.2, C84.2, C85.1, C86.2, C87.2, C89.2, C90.1, C91.2, C92.2, C93.2, C94.1, C95.2, C97.2, C98.2, C100.2, C101.2, C102.2, D3.2 (A), D4.1 (K), D5.1 (K), D9.1 (K), D10.1 (K), D12.2 (A), D13.2 (A), D18.1 (K), D19.2 (A), D28.1 (K), J1.2, J2.3, J2.5, J2.9, J3.2, J6.2 (Ext), J7.2 (Ext), J8.2 (Ext), J9.2 (Ext), J10.2 (Ext), J11.4, J12.4, J13.2, J13.3, J14.2, J14.3, J16.1, J17.A1 (GND), J17.A12 (GND), J17.B1 (GND), J17.B12 (GND), J17.S1 (SHIELD), J18.14, J19.2 (Ext), J20.2 (Ext), J21.2 (Ext), J22.2 (Ext), J25.2 (Ext), J26.2 (Ext), J27.2 (Ext), J28.2 (Ext), J29.5, J29.6, J29.11, J29.12, J30.2 (Ext), J31.2 (Ext), J32.19, J32.20, J32.25, J32.26, J33.2, JP3.2, JP4.2, K1.3 (2), K5.8 (5), K6.8 (5), K7.3 (2), K12.3 (2), K12.10 (7), K13.5 (4), K13.8 (5), K18.4 (3), Q1.3 (S), Q2.3 (S), Q3.3 (S), Q4.3 (S), Q5.3 (S), Q6.3 (S), Q7.3 (S), Q8.3 (S), Q9.3 (S), Q10.3 (S), Q11.3 (S), Q12.3 (S), Q13.3 (S), Q14.3 (S), Q15.3 (S), Q18.3 (S), Q19.3 (S), Q20.3 (S), Q21.3 (S), Q22.3 (S), Q23.3 (S), Q24.3 (S), Q25.3 (S), R2.2, R3.2, R5.2, R9.2, R12.1, R13.1, R14.1, R15.1, R16.2, R17.1, R18.2, R20.1, R21.1, R24.1, R25.1, R26.1, R29.2, R30.1, R33.2, R35.2, R36.1, R44.2, R45.2, R48.1, R49.1, R52.1, R53.1, R57.2, R59.1, R62.2, R63.2, R65.2, R69.2, R70.2, R74.2, R76.2, R82.2, R84.2, R87.2, R89.2, R91.2, R94.2, R96.2, R97.2, R100.2, R103.2, R105.2, R107.2, R108.2, SW1.2, SW2.2, SW3.2, U1.2 (-VINGND), U1.6 (GND), U3.4 (GND), U4.4 (GND), U5.1 (GND), U6.1 (GND), U8.2 (DGND), U8.9 (REF), U9.2 (DGND), U9.9 (REF), U11.1 (-IN), U11.2 (DGND), U11.9 (REF), U12.1 (-IN), U12.2 (DGND), U12.9 (REF), U13.4 (GND), U14.1 (GND), U16.3 (GND), U16.4 (*E2), U18.1 (X1), U18.3 (Y1), U19.1 (-VINGND), U19.7 (-VOUT), U20.12 (VSSA), U20.18 (VSS), U20.31 (VSS), U20.47 (VSS), U20.60 (BOOT0), U20.63 (VSS), U21.2 (GND)
Gain_CS_IN: R75.2, R109.2, U17.4 (Y2), U17.7 (OUT)
Gain_CS_OUT: K11.4 (3), K21.4 (3), U17.3 (Y1), U18.2 (X2)
I+_2_stim+_COM: R100.1, R102.2, U20.35 (PB14)
I-_2_stim-_COM: R87.1, R88.2, U20.40 (PC9)
IO6: J29.28, J32.4
IO7: J29.30, J32.2
I_load: C74.2, K10.3 (2), K16.4 (3)
I_load-: C71.2, K7.4 (3), K10.10 (7)
I_load-_Cout: C71.1, K8.9 (6), K10.9 (6), R56.1, R57.1, U15.3 (VIN+)
I_load_Cout: C74.1, C80.2, K10.4 (3), R56.2, R58.1, U15.2 (VIN-)
Iin+: K13.4 (3), U17.1 (X1)
Iin-: K13.9 (6), U17.2 (X2)
Istim-: K9.5 (4), K15.4 (3), U18.4 (Y2), U18.7 (OUT)
unnamed: C3.2, U20.5 (PD0), Y1.1
unnamed: C5.2, U20.6 (PD1), Y1.2
unnamed: C6.2, C10.1, L1.1, U1.5 (-VOUT)
unnamed: C7.1, C11.1, L2.1, U1.7 (+VOUT)
unnamed: C8.1, C12.1, L3.1, U19.6 (+VOUT)
unnamed: C18.1, C22.1, J4.4, U3.5 (~SHDN), U3.8 (IN)
unnamed: C19.1, C24.1, J5.4, U4.5 (~SHDN), U4.8 (IN)
unnamed: C20.2, C29.1, J4.3, U5.2 (VIN)
unnamed: C21.2, C30.1, J5.3, U6.2 (VIN)
unnamed: C26.1, R11.1, U7.3 (VIN+)
unnamed: C41.1, U5.3 (BYP)
unnamed: C42.2, U3.3 (BYP)
unnamed: C43.1, U6.3 (BYP)
unnamed: C44.2, U4.3 (BYP)
unnamed: C57.1, R38.2, U11.10 (+IN)
unnamed: C58.1, R39.2, U12.10 (+IN)
unnamed: C59.1, R34.2, R42.1, U10.8 (VIN+)
unnamed: C59.2, R42.2, R55.1, U10.5 (VOUT-)
unnamed: C60.1, R36.2, R43.1, U10.1 (VIN-)
unnamed: C60.2, R43.2, R54.1, U10.4 (VOUT+)
unnamed: C72.1, C76.1, J15.4, U13.5 (~SHDN), U13.8 (IN)
unnamed: C75.2, C78.1, J15.3, U14.2 (VIN)
unnamed: C80.1, R58.2, R79.1, U15.6 (VOUT-)
unnamed: C82.1, U14.3 (BYP)
unnamed: C83.2, U13.3 (BYP)
unnamed: C88.2, R80.1, U2.2 (-IN)
unnamed: C91.1, R81.2
unnamed: D1.1 (K), R2.1
unnamed: D2.1 (K), R3.1
unnamed: D3.1 (K), R6.1
unnamed: D4.2 (A), R7.1
unnamed: D5.2 (A), R8.2
unnamed: D6.2 (A), K1.12 (8), Q1.1 (D)
unnamed: D7.2 (A), K2.12 (8), Q2.1 (D)
unnamed: D8.2 (A), K3.12 (8), Q3.1 (D)
unnamed: D9.2 (A), R40.1
unnamed: D10.2 (A), R41.1
unnamed: D11.2 (A), K4.12 (8), Q4.1 (D)
unnamed: D12.1 (K), R46.1
unnamed: D13.1 (K), R47.1
unnamed: D14.2 (A), K5.12 (8), Q5.1 (D)
unnamed: D15.2 (A), K6.12 (8), Q6.1 (D)
unnamed: D16.2 (A), K7.12 (8), Q7.1 (D)
unnamed: D17.2 (A), K8.12 (8), Q8.1 (D)
unnamed: D18.2 (A), R67.1
unnamed: D19.1 (K), R68.1
unnamed: D20.2 (A), K9.12 (8), Q9.1 (D)
unnamed: D21.2 (A), K10.12 (8), Q10.1 (D)
unnamed: D22.2 (A), K11.12 (8), Q11.1 (D)
unnamed: D23.2 (A), K12.12 (8), Q12.1 (D)
unnamed: D24.2 (A), K13.12 (8), Q13.1 (D)
unnamed: D25.2 (A), K14.12 (8), Q14.1 (D)
unnamed: D26.2 (A), K15.12 (8), Q15.1 (D)
unnamed: D27.2 (A), K16.12 (8), Q18.1 (D)
unnamed: D28.2 (A), R93.2
unnamed: D29.2 (A), K17.12 (8), Q19.1 (D)
unnamed: D30.2 (A), K18.12 (8), Q20.1 (D)
unnamed: D31.2 (A), K19.12 (8), Q21.1 (D)
unnamed: D32.2 (A), K20.12 (8), Q22.1 (D)
unnamed: D33.2 (A), K21.12 (8), Q23.1 (D)
unnamed: D34.2 (A), K22.12 (8), Q24.1 (D)
unnamed: D35.2 (A), K23.12 (8), Q25.1 (D)
unnamed: D36.1 (K), R107.1
unnamed: D37.1 (K), R108.1
unnamed: F1.2, Q26.3 (S), Q27.3 (S), U16.8 (VS)
unnamed: K7.5 (4), K9.4 (3)
unnamed: K8.5 (4), R84.1
unnamed: K11.3 (2), RV1.1, RV1.2
unnamed: K11.5 (4), RV2.1, RV2.2
unnamed: Q1.2 (G), R10.1
unnamed: Q2.2 (G), R22.1
unnamed: Q3.2 (G), R23.1
unnamed: Q4.2 (G), R37.1
unnamed: Q5.2 (G), R50.1
unnamed: Q6.2 (G), R51.1
unnamed: Q7.2 (G), R64.1
unnamed: Q8.2 (G), R66.1
unnamed: Q9.2 (G), R71.1
unnamed: Q10.2 (G), R72.1
unnamed: Q11.2 (G), R73.1
unnamed: Q12.2 (G), R77.1
unnamed: Q13.2 (G), R78.1
unnamed: Q14.2 (G), R83.1
unnamed: Q15.2 (G), R88.1
unnamed: Q18.2 (G), R90.1
unnamed: Q19.2 (G), R92.1
unnamed: Q20.2 (G), R95.1
unnamed: Q21.2 (G), R98.1
unnamed: Q22.2 (G), R99.1
unnamed: Q23.2 (G), R102.1
unnamed: Q24.2 (G), R104.1
unnamed: Q25.2 (G), R106.1
unnamed: Q26.1 (G), U16.10 (G1)
unnamed: Q27.1 (G), U16.6 (G2)
unnamed: R12.2, R19.1, U7.2 (VIN-)
unnamed: R26.2, R27.1, U5.4 (ADJ)
unnamed: R28.2, R29.1, U3.2 (ADJ)
unnamed: R30.2, R31.1, U6.4 (ADJ)
unnamed: R32.2, R33.1, U4.2 (ADJ)
unnamed: R38.1, U8.7 (OUT)
unnamed: R39.1, U9.7 (OUT)
unnamed: R59.2, R60.1, U14.4 (ADJ)
unnamed: R61.2, R62.1, U13.2 (ADJ)
unnamed: R75.1, RV1.3
unnamed: R109.1, RV2.3
PWR+: J29.8, J32.24
PWR-: J29.7, J32.23
STIM+_coupling: C96.2, J22.1 (In), J23.1, J24.4, K19.5 (4), K20.9 (6)
STIM-: C99.1, K14.5 (4), K15.5 (4), K16.5 (4), K18.5 (4), K20.5 (4)
STIM-_coupling: C99.2, J21.1 (In), J23.4, J24.1, K20.4 (3), K22.5 (4)
STIM_INPUT_COM: R35.1, R37.2, U20.57 (PB5)
TIA+: K8.4 (3), R79.2
TIA_2_CH2_COM: R65.1, R66.2, U20.61 (PB8)
TIA_Select_1_COM: R63.1, R64.2, U20.58 (PB6)
TIA_Select_2_COM: R69.1, R71.2, U20.59 (PB7)
TIA_coupling_COM: R70.1, R72.2, U20.62 (PB9)
TR1: J29.14, J32.18, U20.25 (PC5)
TR2: J29.13, J32.17, U20.24 (PC4)
V+_2_stim+_COM: R105.1, R106.2, U20.36 (PB15)
V-_2_stim-_COM: R82.1, R83.2, U20.51 (PC10)
VCC: C2.1, F1.1, U1.1 (+VINVCC), U19.2 (+VINVCC)
V_amp: K12.5 (4), R19.2, R34.1, U7.6 (VOUT-)
Vfb_volta: K12.9 (6), R80.2
Vin: K4.4 (3), R11.2
Vin+_ch1: C37.1, J9.1 (In), J14.1, J19.1 (In), J23.2, J24.3, K3.3 (2), K19.4 (3)
Vin+_ch2: C35.1, J7.1 (In), J13.1, K2.3 (2), K8.3 (2)
Vin-_ch1: C38.2, J10.1 (In), J14.4, J20.1 (In), J23.3, J24.2, K3.10 (7), K22.4 (3)
Vin-_ch2: C36.2, J8.1 (In), J13.4, K2.10 (7), K8.10 (7)
Vin_DC: J1.1, Q26.2 (D), U16.2 (E1), U16.9 (V1)
Vin_USB: J17.A4 (VBUS), J17.A9 (VBUS), J17.B4 (VBUS), J17.B9 (VBUS), Q27.2 (D), U16.7 (V2)
Vout+: K13.3 (2), K23.4 (3), R54.2
Vout-: K9.3 (2), K13.10 (7), K14.4 (3), R55.2
Vref_volta: K12.4 (3), U2.3 (+IN)
WE_REF: C88.1, K17.4 (3), R81.1, U2.6 (OUT)
ch1+_Cout: C37.2, K3.4 (3), R17.2, U9.10 (+IN)
ch1-_Cout: C38.1, K3.9 (6), R14.2, U9.1 (-IN)
ch1_out: J12.2, K6.5 (4), U12.7 (OUT)
ch2+_Cout: C35.2, K2.4 (3), R15.2, U8.10 (+IN)
ch2-_Cout: C36.1, K2.9 (6), R13.2, U8.1 (-IN)
ch2_out: J11.2, K5.5 (4), U11.7 (OUT)
gnd_2_stim-_COM: R94.1, R95.2, U20.53 (PC12)
scope1+: J28.1 (In), J29.2, J32.30, K6.4 (3), K12.8 (5)
scope1-: J25.1 (In), J29.1, J32.29, JP3.1, K6.9 (6)
scope2+: J29.4, J31.1 (In), J32.28, K5.4 (3)
scope2-: J26.1 (In), J29.3, J32.27, JP4.1, K5.9 (6)
stim_coupling_COM: R97.1, R99.2, U20.2 (PC13)
tia_2_stim-_COM: R89.1, R90.2, U20.52 (PC11)
volta_2_stim+_COM: R91.1, R92.2, U20.34 (PB13)
volta_EN_COM: R74.1, R77.2, U20.29 (PB10)

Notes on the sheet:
STM32F103
STLink Prog Connector
STM32 Status LEDs
Tactile SWITCHES
Voltage source
TIA
Stim LDOs
Fcut = 19 MHz
G = 2.2
Current Source
Potentiostat FB
Power Supply
STIM + Sel
STIM - Sel
Stim Coupling
4 - 2 wires mode
Electrode Conn
AD2 Conn
Fcut = 16 MHz
Channel 1
Channel 2

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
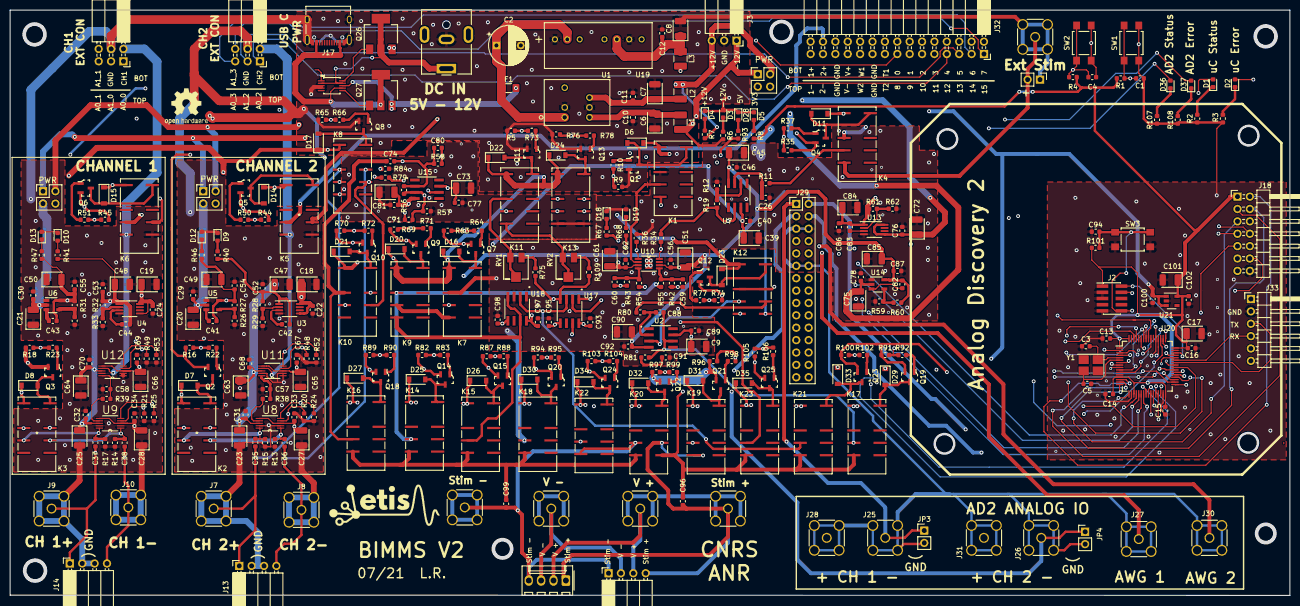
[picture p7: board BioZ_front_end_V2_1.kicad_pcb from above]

Board: 4 copper layers, 262.5 x 120.1 mm, 360 parts (0 on the bottom side), 220 nets.

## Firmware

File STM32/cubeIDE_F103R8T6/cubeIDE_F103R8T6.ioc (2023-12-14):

#MicroXplorer Configuration settings - do not modify
File.Version=6
GPIO.groupedBy=Group By Peripherals
KeepUserPlacement=false
Mcu.CPN=STM32F103R8T6
Mcu.Family=STM32F1
Mcu.IP0=NVIC
Mcu.IP1=RCC
Mcu.IP2=SPI1
Mcu.IP3=SYS
Mcu.IP4=TIM2
Mcu.IPNb=5
Mcu.Name=STM32F103R(8-B)Tx
Mcu.Package=LQFP64
Mcu.Pin0=PC13-TAMPER-RTC
Mcu.Pin1=PC14-OSC32_IN
Mcu.Pin10=PA5
Mcu.Pin11=PA6
Mcu.Pin12=PA7
Mcu.Pin13=PB0
Mcu.Pin14=PB1
Mcu.Pin15=PB2
Mcu.Pin16=PB10
Mcu.Pin17=PB11
Mcu.Pin18=PB12
Mcu.Pin19=PB13
Mcu.Pin2=PC15-OSC32_OUT
Mcu.Pin20=PB14
Mcu.Pin21=PB15
Mcu.Pin22=PC9
Mcu.Pin23=PA13
Mcu.Pin24=PA14
Mcu.Pin25=PC10
Mcu.Pin26=PC11
Mcu.Pin27=PC12
Mcu.Pin28=PB3
Mcu.Pin29=PB4
Mcu.Pin3=PD0-OSC_IN
Mcu.Pin30=PB5
Mcu.Pin31=PB6
Mcu.Pin32=PB7
Mcu.Pin33=PB8
Mcu.Pin34=PB9
Mcu.Pin35=VP_SYS_VS_Systick
Mcu.Pin36=VP_TIM2_VS_ClockSourceINT
Mcu.Pin4=PD1-OSC_OUT
Mcu.Pin5=PC0
Mcu.Pin6=PC1
Mcu.Pin7=PC2
Mcu.Pin8=PC3
Mcu.Pin9=PA4
Mcu.PinsNb=37
Mcu.ThirdPartyNb=0
Mcu.UserConstants=
Mcu.UserName=STM32F103R8Tx
MxCube.Version=6.6.1
MxDb.Version=DB.6.0.60
NVIC.BusFault_IRQn=true\:0\:0\:false\:false\:true\:false\:false\:false
NVIC.DebugMonitor_IRQn=true\:0\:0\:false\:false\:true\:false\:false\:false
NVIC.EXTI4_IRQn=true\:10\:0\:true\:false\:true\:true\:true\:true
NVIC.ForceEnableDMAVector=true
NVIC.HardFault_IRQn=true\:0\:0\:false\:false\:true\:false\:false\:false
NVIC.MemoryManagement_IRQn=true\:0\:0\:false\:false\:true\:false\:false\:false
NVIC.NonMaskableInt_IRQn=true\:0\:0\:false\:false\:true\:false\:false\:false
NVIC.PendSV_IRQn=true\:0\:0\:false\:false\:true\:false\:false\:false
NVIC.PriorityGroup=NVIC_PRIORITYGROUP_4
NVIC.SVCall_IRQn=true\:0\:0\:false\:false\:true\:false\:false\:false
NVIC.SysTick_IRQn=true\:15\:0\:false\:false\:true\:false\:true\:false
NVIC.TIM2_IRQn=true\:0\:0\:false\:false\:true\:true\:true\:true
NVIC.UsageFault_IRQn=true\:0\:0\:false\:false\:true\:false\:false\:false
PA13.Mode=Serial_Wire
PA13.Signal=SYS_JTMS-SWDIO
PA14.Mode=Serial_Wire
PA14.Signal=SYS_JTCK-SWCLK
PA4.GPIOParameters=GPIO_PuPd,GPIO_Label,GPIO_ModeDefaultEXTI
PA4.GPIO_Label=SS
PA4.GPIO_ModeDefaultEXTI=GPIO_MODE_IT_FALLING
PA4.GPIO_PuPd=GPIO_PULLUP
PA4.Locked=true
PA4.Signal=GPXTI4
PA5.Mode=Full_Duplex_Slave
PA5.Signal=SPI1_SCK
PA6.Mode=Full_Duplex_Slave
PA6.Signal=SPI1_MISO
PA7.Mode=Full_Duplex_Slave
PA7.Signal=SPI1_MOSI
PB0.GPIOParameters=GPIO_Label
PB0.GPIO_Label=relay1
PB0.Locked=true
PB0.Signal=GPIO_Output
PB1.GPIOParameters=GPIO_Label
PB1.GPIO_Label=relay2
PB1.Locked=true
PB1.Signal=GPIO_Output
PB10.GPIOParameters=GPIO_Label
PB10.GPIO_Label=relay11
PB10.Locked=true
PB10.Signal=GPIO_Output
PB11.GPIOParameters=GPIO_Label
PB11.GPIO_Label=relay12
PB11.Locked=true
PB11.Signal=GPIO_Output
PB12.GPIOParameters=GPIO_Label
PB12.GPIO_Label=relay13
PB12.Locked=true
PB12.Signal=GPIO_Output
PB13.GPIOParameters=GPIO_Label
PB13.GPIO_Label=relay14
PB13.Locked=true
PB13.Signal=GPIO_Output
PB14.GPIOParameters=GPIO_Label
PB14.GPIO_Label=relay15
PB14.Locked=true
PB14.Signal=GPIO_Output
PB15.GPIOParameters=GPIO_Label
PB15.GPIO_Label=relay16
PB15.Locked=true
PB15.Signal=GPIO_Output
PB2.GPIOParameters=GPIO_Label
PB2.GPIO_Label=relay3
PB2.Locked=true
PB2.Signal=GPIO_Output
PB3.GPIOParameters=GPIO_Label
PB3.GPIO_Label=relay4
PB3.Locked=true
PB3.Signal=GPIO_Output
PB4.GPIOParameters=GPIO_Label
PB4.GPIO_Label=relay5
PB4.Locked=true
PB4.Signal=GPIO_Output
PB5.GPIOParameters=GPIO_Label
PB5.GPIO_Label=relay6
PB5.Locked=true
PB5.Signal=GPIO_Output
PB6.GPIOParameters=GPIO_Label
PB6.GPIO_Label=relay7
PB6.Locked=true
PB6.Signal=GPIO_Output
PB7.GPIOParameters=GPIO_Label
PB7.GPIO_Label=relay8
PB7.Locked=true
PB7.Signal=GPIO_Output
PB8.GPIOParameters=GPIO_Label
PB8.GPIO_Label=relay9
PB8.Locked=true
PB8.Signal=GPIO_Output
PB9.GPIOParameters=GPIO_Label
PB9.GPIO_Label=relay10
PB9.Locked=true
PB9.Signal=GPIO_Output
PC0.GPIOParameters=GPIO_Label
PC0.GPIO_Label=errorLED
PC0.Locked=true
PC0.Signal=GPIO_Output
PC1.GPIOParameters=GPIO_Label
PC1.GPIO_Label=statusLED
PC1.Locked=true
PC1.Signal=GPIO_Output
PC10.GPIOParameters=GPIO_Label
PC10.GPIO_Label=relay18
PC10.Locked=true
PC10.Signal=GPIO_Output
PC11.GPIOParameters=GPIO_Label
PC11.GPIO_Label=relay19
PC11.Locked=true
PC11.Signal=GPIO_Output
PC12.GPIOParameters=GPIO_Label
PC12.GPIO_Label=relay20
PC12.Locked=true
PC12.Signal=GPIO_Output
PC13-TAMPER-RTC.GPIOParameters=GPIO_Label
PC13-TAMPER-RTC.GPIO_Label=relay21
PC13-TAMPER-RTC.Locked=true
PC13-TAMPER-RTC.Signal=GPIO_Output
PC14-OSC32_IN.GPIOParameters=GPIO_Label
PC14-OSC32_IN.GPIO_Label=relay22
PC14-OSC32_IN.Locked=true
PC14-OSC32_IN.Signal=GPIO_Output
PC15-OSC32_OUT.GPIOParameters=GPIO_Label
PC15-OSC32_OUT.GPIO_Label=relay23
PC15-OSC32_OUT.Locked=true
PC15-OSC32_OUT.Signal=GPIO_Output
PC2.GPIOParameters=GPIO_Label
PC2.GPIO_Label=SW1
PC2.Locked=true
PC2.Signal=GPIO_Input
PC3.GPIOParameters=GPIO_Label
PC3.GPIO_Label=SW2
PC3.Locked=true
PC3.Signal=GPIO_Input
PC9.GPIOParameters=GPIO_Label
PC9.GPIO_Label=relay17
PC9.Locked=true
PC9.Signal=GPIO_Output
PD0-OSC_IN.Mode=HSE-External-Clock-Source
PD0-OSC_IN.Signal=RCC_OSC_IN
PD1-OSC_OUT.Mode=HSE-External-Clock-Source
PD1-OSC_OUT.Signal=RCC_OSC_OUT
PinOutPanel.RotationAngle=0
ProjectManager.AskForMigrate=true
ProjectManager.BackupPrevious=false
ProjectManager.CompilerOptimize=6
ProjectManager.ComputerToolchain=false
ProjectManager.CoupleFile=false
ProjectManager.CustomerFirmwarePackage=
ProjectManager.DefaultFWLocation=true
ProjectManager.DeletePrevious=true
ProjectManager.DeviceId=STM32F103R8Tx
ProjectManager.FirmwarePackage=STM32Cube FW_F1 V1.8.5
ProjectManager.FreePins=false
ProjectManager.HalAssertFull=false
ProjectManager.HeapSize=0x200
ProjectManager.KeepUserCode=true
ProjectManager.LastFirmware=true
ProjectManager.LibraryCopy=2
ProjectManager.MainLocation=Core/Src
ProjectManager.NoMain=false
ProjectManager.PreviousToolchain=
ProjectManager.ProjectBuild=false
ProjectManager.ProjectFileName=cubeIDE_F103R8T6.ioc
ProjectManager.ProjectName=cubeIDE_F103R8T6
ProjectManager.RegisterCallBack=
ProjectManager.StackSize=0x400
ProjectManager.TargetToolchain=STM32CubeIDE
ProjectManager.ToolChainLocation=
ProjectManager.UnderRoot=true
ProjectManager.functionlistsort=1-SystemClock_Config-RCC-false-HAL-false
RCC.ADCFreqValue=36000000
RCC.AHBFreq_Value=72000000
RCC.APB1CLKDivider=RCC_HCLK_DIV2
RCC.APB1Freq_Value=36000000
RCC.APB1TimFreq_Value=72000000
RCC.APB2Freq_Value=72000000
RCC.APB2TimFreq_Value=72000000
RCC.FCLKCortexFreq_Value=72000000
RCC.FamilyName=M
RCC.HCLKFreq_Value=72000000
RCC.IPParameters=ADCFreqValue,AHBFreq_Value,APB1CLKDivider,APB1Freq_Value,APB1TimFreq_Value,APB2Freq_Value,APB2TimFreq_Value,FCLKCortexFreq_Value,FamilyName,HCLKFreq_Value,MCOFreq_Value,PLLCLKFreq_Value,PLLMCOFreq_Value,PLLMUL,PLLSourceVirtual,SYSCLKFreq_VALUE,SYSCLKSource,TimSysFreq_Value,USBFreq_Value,VCOOutput2Freq_Value
RCC.MCOFreq_Value=72000000
RCC.PLLCLKFreq_Value=72000000
RCC.PLLMCOFreq_Value=36000000
RCC.PLLMUL=RCC_PLL_MUL9
RCC.PLLSourceVirtual=RCC_PLLSOURCE_HSE
RCC.SYSCLKFreq_VALUE=72000000
RCC.SYSCLKSource=RCC_SYSCLKSOURCE_PLLCLK
RCC.TimSysFreq_Value=72000000
RCC.USBFreq_Value=72000000
RCC.VCOOutput2Freq_Value=8000000
SH.GPXTI4.0=GPIO_EXTI4
SH.GPXTI4.ConfNb=1
SPI1.CLKPhase=SPI_PHASE_2EDGE
SPI1.CLKPolarity=SPI_POLARITY_HIGH
SPI1.Direction=SPI_DIRECTION_2LINES
SPI1.IPParameters=VirtualType,Mode,Direction,CLKPolarity,CLKPhase
SPI1.Mode=SPI_MODE_SLAVE
SPI1.VirtualType=VM_SLAVE
TIM2.IPParameters=Prescaler,Period
TIM2.Period=7200
TIM2.Prescaler=100
VP_SYS_VS_Systick.Mode=SysTick
VP_SYS_VS_Systick.Signal=SYS_VS_Systick
VP_TIM2_VS_ClockSourceINT.Mode=Internal
VP_TIM2_VS_ClockSourceINT.Signal=TIM2_VS_ClockSourceINT
board=custom
isbadioc=false

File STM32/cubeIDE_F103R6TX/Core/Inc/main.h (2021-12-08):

/* USER CODE BEGIN Header */
/**
  ******************************************************************************
  * @file           : main.h
  * @brief          : Header for main.c file.
  *                   This file contains the common defines of the application.
  ******************************************************************************
  * @attention
  *
  * <h2><center>&copy; Copyright (c) 2021 STMicroelectronics.
  * All rights reserved.</center></h2>
  *
  * This software component is licensed by ST under BSD 3-Clause license,
  * the "License"; You may not use this file except in compliance with the
  * License. You may obtain a copy of the License at:
  *                        opensource.org/licenses/BSD-3-Clause
  *
  ******************************************************************************
  */
/* USER CODE END Header */

/* Define to prevent recursive inclusion -------------------------------------*/
#ifndef __MAIN_H
#define __MAIN_H

#ifdef __cplusplus
extern "C" {
#endif

/* Includes ------------------------------------------------------------------*/
#include "stm32f1xx_hal.h"

/* Private includes ----------------------------------------------------------*/
/* USER CODE BEGIN Includes */
#define DEVICE_ID         0x09

#define Relay_Default     0b00000000000000000000000

//STM32 Globlal State
#define off_state       0
#define idle_state      1
#define locked_state    2
#define error_state     3

//Command
#define set_state  0x01
#define set_relays 0x02
#define read_reg   0x03

//Mask for incomming data
#define Mask_data 0x00FFFFFFF
#define shift_com 29

#define SLOW_BLINK  1s
#define FAST_BLINK  100ms

//Register Address map for reading
#define ID_add          0
#define state_add       1
#define error_add       2
#define relays_map_add  3

/* USER CODE END Includes */

/* Exported types ------------------------------------------------------------*/
/* USER CODE BEGIN ET */

/* USER CODE END ET */

/* Exported constants --------------------------------------------------------*/
/* USER CODE BEGIN EC */

/* USER CODE END EC */

/* Exported macro ------------------------------------------------------------*/
/* USER CODE BEGIN EM */

/* USER CODE END EM */

/* Exported functions prototypes ---------------------------------------------*/
void Error_Handler(void);

/* USER CODE BEGIN EFP */

/* USER CODE END EFP */

/* Private defines -----------------------------------------------------------*/
#define relay21_Pin GPIO_PIN_13
#define relay21_GPIO_Port GPIOC
#define relay22_Pin GPIO_PIN_14
#define relay22_GPIO_Port GPIOC
#define relay23_Pin GPIO_PIN_15
#define relay23_GPIO_Port GPIOC
#define errorLED_Pin GPIO_PIN_0
#define errorLED_GPIO_Port GPIOC
#define statusLED_Pin GPIO_PIN_1
#define statusLED_GPIO_Port GPIOC
#define SW1_Pin GPIO_PIN_2
#define SW1_GPIO_Port GPIOC
#define SW2_Pin GPIO_PIN_3
#define SW2_GPIO_Port GPIOC
#define SS_Pin GPIO_PIN_4
#define SS_GPIO_Port GPIOA
#define SS_EXTI_IRQn EXTI4_IRQn
#define relay1_Pin GPIO_PIN_0
#define relay1_GPIO_Port GPIOB
#define relay2_Pin GPIO_PIN_1
#define relay2_GPIO_Port GPIOB
#define relay3_Pin GPIO_PIN_2
#define relay3_GPIO_Port GPIOB
#define relay11_Pin GPIO_PIN_10
#define relay11_GPIO_Port GPIOB
#define relay12_Pin GPIO_PIN_11
#define relay12_GPIO_Port GPIOB
#define relay13_Pin GPIO_PIN_12
#define relay13_GPIO_Port GPIOB
#define relay14_Pin GPIO_PIN_13
#define relay14_GPIO_Port GPIOB
#define relay15_Pin GPIO_PIN_14
#define relay15_GPIO_Port GPIOB
#define relay16_Pin GPIO_PIN_15
#define relay16_GPIO_Port GPIOB
#define relay17_Pin GPIO_PIN_9
#define relay17_GPIO_Port GPIOC
#define relay18_Pin GPIO_PIN_10
#define relay18_GPIO_Port GPIOC
#define relay19_Pin GPIO_PIN_11
#define relay19_GPIO_Port GPIOC
#define relay20_Pin GPIO_PIN_12
#define relay20_GPIO_Port GPIOC
#define relay4_Pin GPIO_PIN_3
#define relay4_GPIO_Port GPIOB
#define relay5_Pin GPIO_PIN_4
#define relay5_GPIO_Port GPIOB
#define relay6_Pin GPIO_PIN_5
#define relay6_GPIO_Port GPIOB
#define relay7_Pin GPIO_PIN_6
#define relay7_GPIO_Port GPIOB
#define relay8_Pin GPIO_PIN_7
#define relay8_GPIO_Port GPIOB
#define relay9_Pin GPIO_PIN_8
#define relay9_GPIO_Port GPIOB
#define relay10_Pin GPIO_PIN_9
#define relay10_GPIO_Port GPIOB
/* USER CODE BEGIN Private defines */

/* USER CODE END Private defines */

#ifdef __cplusplus
}
#endif

#endif /* __MAIN_H */

/************************ (C) COPYRIGHT STMicroelectronics *****END OF FILE****/

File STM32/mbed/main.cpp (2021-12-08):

/* mbed Microcontroller Library
 * Copyright (c) 2019 ARM Limited
 * SPDX-License-Identifier: Apache-2.0
*   - Add read relays and registers
*   - Handle error
*   - Clean and comment
*/

#include "DigitalOut.h"
#include "PinNames.h"
#include "SPISlave.h"
#include "mbed.h"
#include "nsapi_types.h"
#include "constants.h"


void decode_data(long int data_from_AD2);
void update_state(long int data);
void send_register(long int add);

void updateRelay(long int RelayValue);

void toggleStatusLED();
void toggleErrorLED();

void InitOffState();
void InitIdleState();
void InitLockedState();
void InitErrorState();

void TX32bitsSPI();
void Data2buff(long int data);
SPISlave SPI_AD2(MOSI_AD2,MISO_AD2,SCLK_AD2,SS_AD2);

// Init LED
DigitalOut status_LED(statusLED);
DigitalOut error_LED(errorLED);

// Init Relays
DigitalOut rly1(relay1);
DigitalOut rly2(relay2);
DigitalOut rly3(relay3);
DigitalOut rly4(relay4);
DigitalOut rly5(relay5);
DigitalOut rly6(relay6);
DigitalOut rly7(relay7);
DigitalOut rly8(relay8);
DigitalOut rly9(relay9);
DigitalOut rly10(relay10);
DigitalOut rly11(relay11);
DigitalOut rly12(relay12);
DigitalOut rly13(relay13);
DigitalOut rly14(relay14);
DigitalOut rly15(relay15);
DigitalOut rly16(relay16);
DigitalOut rly17(relay17);
DigitalOut rly18(relay18);
DigitalOut rly19(relay19);
DigitalOut rly20(relay20);
DigitalOut rly21(relay21);
DigitalOut rly22(relay22);
DigitalOut rly23(relay23);

//Tickers 
Ticker ticker_Status_LED;
Ticker ticker_Error_LED;

//global variable 
long int data_from_AD2;
long int data_to_AD2;
short int rxBuff[4];
short int txBuff[4];
short unsigned int spi_idx;
short unsigned int state,new_32bitsSPI; 
long int relay_state ;

int main()
{
    //Init Global Variables
    for (short unsigned int i = 0; i<4; i++)
        {
           rxBuff[i]=0;
           txBuff[i]=0;
        }
    
    data_from_AD2 = 0;
    new_32bitsSPI = 0;
    spi_idx = 0;

    updateRelay(Relay_Default);

    //Init SPI
    SPI_AD2.format(nbits_spi_AD2,spi_mode_AD2);
    SPI_AD2.frequency(spi_freq_AD2);
    SPI_AD2.reply(0);
   
    //Init state 
    state = off_state ;
    InitOffState();

    while (true) {

        if (SPI_AD2.receive()){             //Read SPI register
            TX32bitsSPI();
        }
        if (new_32bitsSPI)
        {
            decode_data(data_from_AD2);
            new_32bitsSPI = 0;
        }
        switch (state)
        {
            case off_state:
                // Do something 
                break;
            case idle_state:
                // Do Something
                break;
            case locked_state:
                // Do Something
                break;
            case error_state: 
                // Do Something 
                break;
        }

    }
}
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

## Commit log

2021-12-08 add hardware files
    [BOM_FULL.xlsx, BOM_HandSolder.xlsx, BOM_PCBWAY.xlsx, BioZ_front_end_V2_1-B_Cu.gbr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]
2021-12-08 fix commit
    [BOM_FULL.xlsx, BOM_HandSolder.xlsx, BOM_PCBWAY.xlsx, BioZ_front_end_V2_1-B_Cu.gbr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]
2022-01-04 update files
    [BioZ_front_end_V2_1.kicad_pcb, BioZ_front_end_V2_1.sch, potentiostat_EIS.csv]
2022-03-09 Add gain voltage and gain current
2022-12-01 Update BIMMS.py
    adding destructor to bimms
    +
    changing Gain_TIA value to correspond with the new resistor value
2023-10-24 change archi source
    [potentiostat_EIS.csv]
2023-11-15 Bimms calibration
2023-11-16 print except error for debbug
2023-11-16 update test 003 current source
2023-11-21 remove print
2023-12-07 Update examples
    [potentiostat_EIS.csv]
2023-12-07 Update __init__.py
    don't use bash_bimms case
2023-12-14 add STM32F103xxx code
2024-06-04 Bump version: 1.1.2 → 1.1.3

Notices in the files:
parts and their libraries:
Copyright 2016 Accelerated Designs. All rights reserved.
